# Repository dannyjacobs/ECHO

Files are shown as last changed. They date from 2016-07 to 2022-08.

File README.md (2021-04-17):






The External Calibrator for Hydrogen Arrays (ECHO) is a system for calibrating wide-field radio frequency arrays using a radio transmitter mounted on a drone.
Primarily targeting (but not exclusively limited to) arrays operating in the sub-GHz band targeting highly redshifted
21cm radiation from the early universe.

This repository contains software for planning missions and analyzing data. It also contains hardware designs for drones and mounts.

This is an open source project. Use and reuse is encouraged.  If you use this code or hardware designs please reference the github repo.
http://github.com/dannyjacobs/ECHO and cite [our 2017 paper](http://adsabs.harvard.edu/abs/2017PASP..129c5002J).  If you have improvements please fork and send a PR!

## Community
* We have an active "Slack Connect" channel, accessible to anyone with a Slack account.  To be invited, email [Danny Jacobs](dcjacob2@asu.edu)
* Project [Web page](http://danielcjacobs.com/ECHO)
* [Code Documentation](https://external-calibrator-for-hydrogen-arrays-echo.readthedocs.io)
* A [mailing list](https://groups.google.com/d/forum/astro_echo) exists

## Installation
Install prerequisites. We recommend the anaconda package manager
* healpy (note that as of Jan 2020 healpy is not available for Windows)
* matplotlib
* numpy
* scipy

Get this repo
`git clone https://github.com/dannyjacobs/ECHO.git`

Install using pip
```
cd ECHO
pip install .
```

## Organization
The code is organized into a few modules. The beam mapping pipeline steps are
1. Read and down-select drone telemetry
2. Read and down-select radio telescope data (varies per telescope, usually spectra vs time)
3. Match up drone positions and telescope measurements. (Sometimes referred to as zippering.)
4. Grid beam (including power map, sample counts and standard deviation)
5. Analyze results. Example analysis steps include:
  1. subtract transmitter model
  2. plot beam maps
  3. plot slices
  4. plot drone events and dynamics
  5. difference beams
### Modules

 #### `plot_utils.py`
 Functions for plotting, but also all functions relating to healpix gridding
 and manipulation including gridding.
  * `grid_to_healpix` :  grids aligned RF power vs XYZ position
 into a healpix map
  * `make_beam` :  downselects desired spectral channel, converts from latlon to XYZ and calls `grid_to_healpix`
  * `project_healpix` :  flattens from spherical healpix map to 2d gnomic projection
  * `rotate_hpm` :  rotates a healpix map about the polar axis. useful for plotting
  * Other functions, most of whom are deprecated.
 #### `read_utils.py`
 Functions for reading and writing drone and beam data. Drone log file formats
 are not well documented and change all the time.
  * `read_map` : replacement for healpy read function that respects nans
  * `write_map`: replacement for healpy write function that respect nans
  * `apm_version`: tries to determine the version of ardupilot that wrote a log file.
  * `read_apm_log_A_B_C` : reads an ardupilot log of version A_B_C
    * returns position_times, positions,
    * attitude_times, attitudes,
    * waypoint_times, waypoint_numbers
  * `read_echo_spectrum` : reads a spectrum data file output by the ECHO spectrum logger ca 2017 (signalhound + get_sh_spectra)
  * `read_orbcomm_spectrum` : reads a spectrum data file output by the Bradley orbcomm system (ca 2017)
  * `channel_select` : given a spectrum, list of frequencies, and desired frequency returns closest frequency and spectrum amplitude
  * `interp_rx`: interpolates received power onto the measured position time grid
  * `flag_angles` : flags outlier yaws input times,yaw_angles return matching flag array
  * `flag_waypoints` : flags a range of time around a list of waypoints
  * `apply_flagtimes` : Given a list of bad times, a buffer size and a time array, generate a flag table.
#### `position_utils.py`
 * `latlon2xy` : about what you think
 * `to_spherical` : xyz to spherical
#### `time_utils.py`
Most of these are of dubious necessity.
 * `unix_to_gps` : thin wrapper around astropy.Time
 * `gps_to_HMS` : convert GPS time to Hours Minutes Seconds, thin wrapper around
#### `server_utils.py`
Stuff developed to support real-time operations. This never worked very well with mavlink.
### Scripts
#### Jacobs 2017
Scripts used in the 2017 paper are all run in [one master shell script](https://github.com/dannyjacobs/ECHO_paper1/blob/master/scripts/make_plots.sh)
 * plot_yaw.py
 * plot_GB_pos_power_interp.py
 * ECHO_zipper.py
 * ECHO_mk_beam.py
 * plot_ECHO_GB_power_rms_counts.py
 * plot_ECHO_GB_maps.py
 * plot_GB_slices.py
 * ECHO_sub_tx_beam.py
 * plot_ECHO_GB_ratios.py
 * plot_GB_avg_slices.py
 * plot_MWAtile_slices.py
 * MWATilemodel2hpm.py
 * combine_MWAtile_maps.py

 #### Utility Scripts
  * valon_readwrite.py : program the valon transmitter
  * gen_spherical_flight_path.py : generate waypoints in a healpix pattern
  * CST_to_healpix.py : convert the beam file from CST Microwave studio to a healpix map. Note that this should eventually be replaced with [pyuvbeam](https://github.com/RadioAstronomySoftwareGroup/pyuvdata/blob/master/pyuvdata/uvbeam.py).

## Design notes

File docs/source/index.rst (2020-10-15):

.. ECHO documentation master file, created by
   sphinx-quickstart on Mon Jul 13 10:42:31 2020.
   You can adapt this file completely to your liking, but it should at least
   contain the root `toctree` directive.

Welcome to ECHO's documentation!
================================
ECHO is a drone-based system for calibrating wide-field radio arrays seeking to probe the Epoch of Reionization (EoR). The goal is to make accurate in-situ beam maps and incorporate this data into 21cm power spectrum analysis pipelines.
For more details you can read the first demonstration of ECHO paper by Jacobs et al. 2017 here_

This repository contains software used to generate flight plans, collect and reduce resulting data from a calibration run.

.. _here: https://ui.adsabs.harvard.edu/abs/2017PASP..129c5002J/abstract

Workflow
----------
Analysis of data from a calibration run involves three main steps:

* Reading in transmitter position data and receiver spectrum
* Interpolating receiver spectrum to drone flight times
* Gridding data onto a healpix map

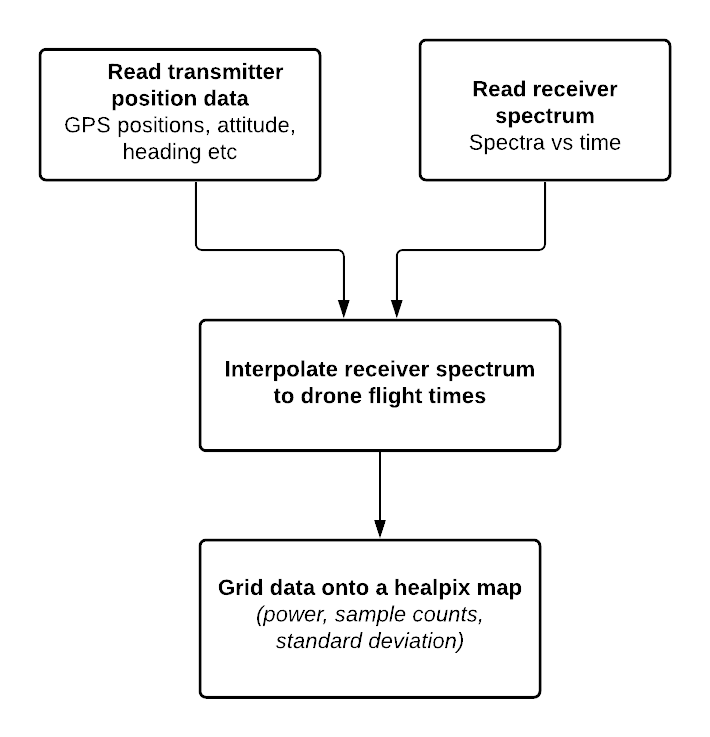
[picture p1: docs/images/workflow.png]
workflow


ECHO setup
------------

LWA-SV '19 setup

Flight Path
-----------------

ECHO follows a spherical shell flight pattern centered around the antenna under test as shown in the figure.

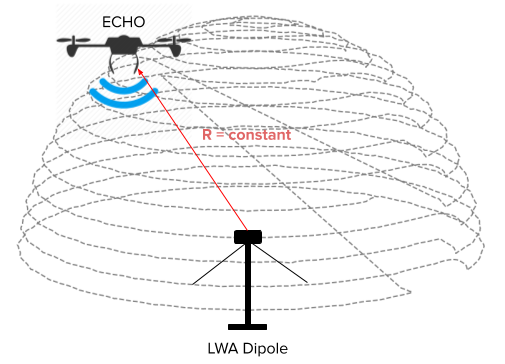
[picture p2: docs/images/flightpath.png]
flight path


.. toctree::
   :caption: Contents:

   Installation <installation>
   Tutorial <tutorial>
   API Reference <api>

Indices and tables
==================

* :ref:`genindex`
* :ref:`modindex`
* :ref:`search`

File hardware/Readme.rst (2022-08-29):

.. csv-table:: ECHO Version Summary
   :header: "Version", "Drone Make", "Drone Frame", "Drone Name", "Tx Mount", "Transmitter", "Antenna", "Flight Software"
   :widths: auto

   "1", "Mystery Inc.", "Octo", "Brain", " ", " ", "BicoLOG 5070", " "
   "2", "Flamewheel", "Quad", "Crater", " ", " ", "BicoLOG 5070", " "
   "3", "3D-Robotics", "X8", Pancake, " ", " ", BicoLOG 5070", " "
   "4", "3D-Robotics", "X8", Waffle, "`Sliding_Mount <https://github.com/dannyjacobs/ECHO/tree/master/hardware/STLs/04_Sliding_Mount>`_", "Blackbox", BicoLOG 5070", " "
   "5", "3D-Robotics", "X8", Killer, "`X8_Mount_v1 <https://github.com/dannyjacobs/ECHO/tree/master/hardware/STLs/05_X8_Mount_v1>`_", "Blackbox", BicoLOG 5070", " "
   "6", "Steadidrone Vader", "X8", "Vader", "`Vader_Mount <https://github.com/dannyjacobs/ECHO/tree/master/hardware/STLs/06_Vader_Mount>`_", "Blackbox", "BicoLOG 5070", "PX4"
   "7", "Yuneec", "Octo H520", "Yuneec", "`Yuneec_Mount <https://github.com/dannyjacobs/ECHO/tree/master/hardware/STLs/07_Yuneec_Mount>`_", "Valon 5009", "BicoLOG 5070", "Yuneec"
   "8", "3D-Robotics", "X8", "Killer", "`X8_Mount_v2 <https://github.com/dannyjacobs/ECHO/tree/master/hardware/STLs/08_X8_Mount_v2>`_", "Valon 5009", "BicoLOG 5070", "PX4"
   "9", "in house `bom <https://github.com/dannyjacobs/ECHO/blob/master/hardware/Chiropter%20BoM%20-%20Revised%20Build%20Sheet.pdf>`_, `build log <https://github.com/dannyjacobs/ECHO/blob/master/hardware/Chiropter%20Build%20Log.pdf>`_","Hex F550", "Chiropter", "`Chiropter Mount v1 (for Valon) <https://github.com/dannyjacobs/ECHO/tree/master/hardware/STLs/09_Chiropter_Mount_v1>`_, `Mount V2 for TituTx etc  <https://github.com/dannyjacobs/ECHO/tree/master/hardware/STLs/10_Chiropter_Mount_v2>`_","Valon 5009","BicoLOG 5070","PX4"

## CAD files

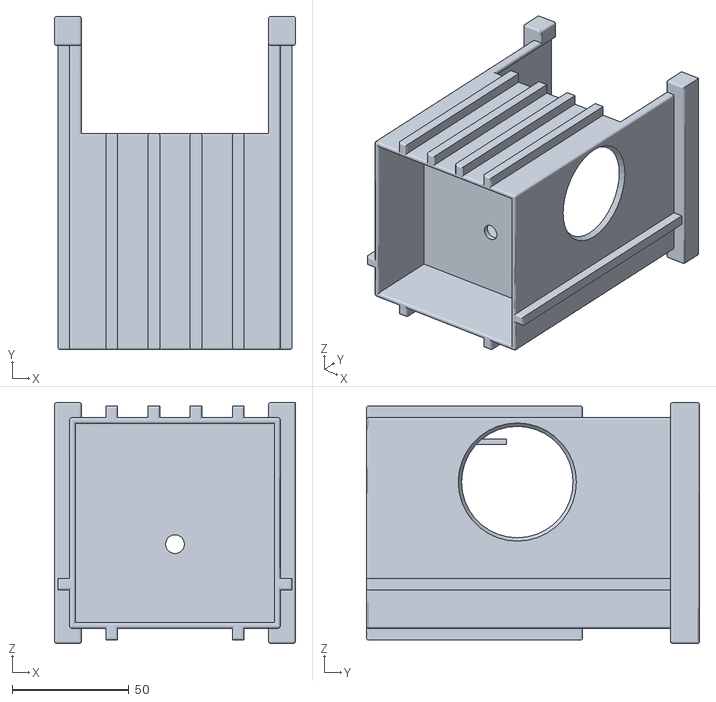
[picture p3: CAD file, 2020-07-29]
hardware/STLs/04_Sliding_Mount/Sliding_Mount_Bottom.STL
103.0 x 142.5 x 103.0

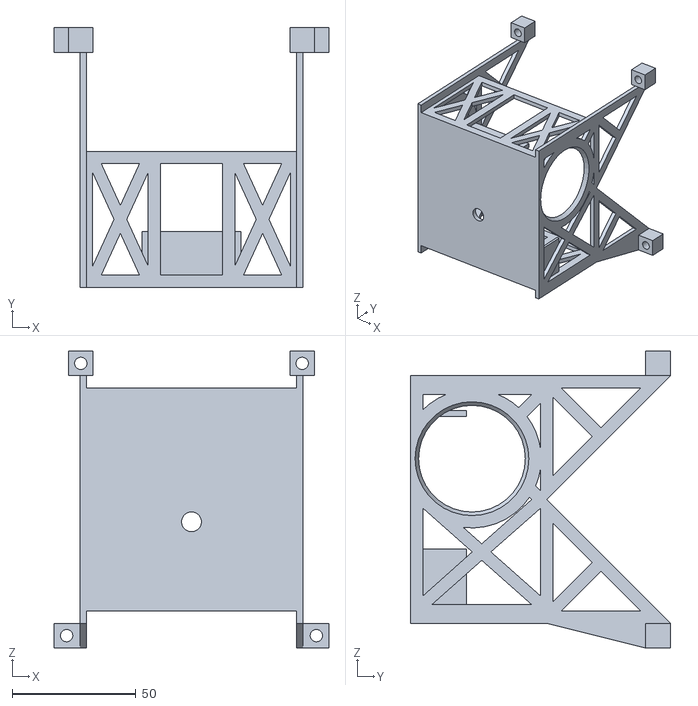
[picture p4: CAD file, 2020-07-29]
hardware/STLs/05_X8_Mount_v1/X8_Mount_v1.STL
111.0 x 105.0 x 120.1

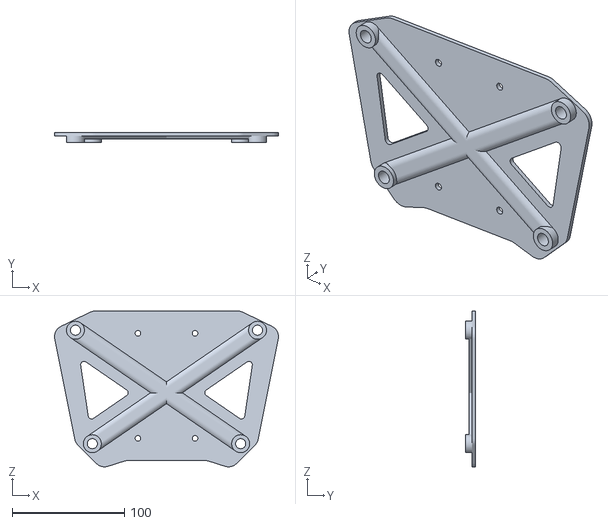
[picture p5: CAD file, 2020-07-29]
hardware/STLs/06_Vader_Mount/Vader_Adapter_Plate.STL
199.3 x 9.00 x 138.6

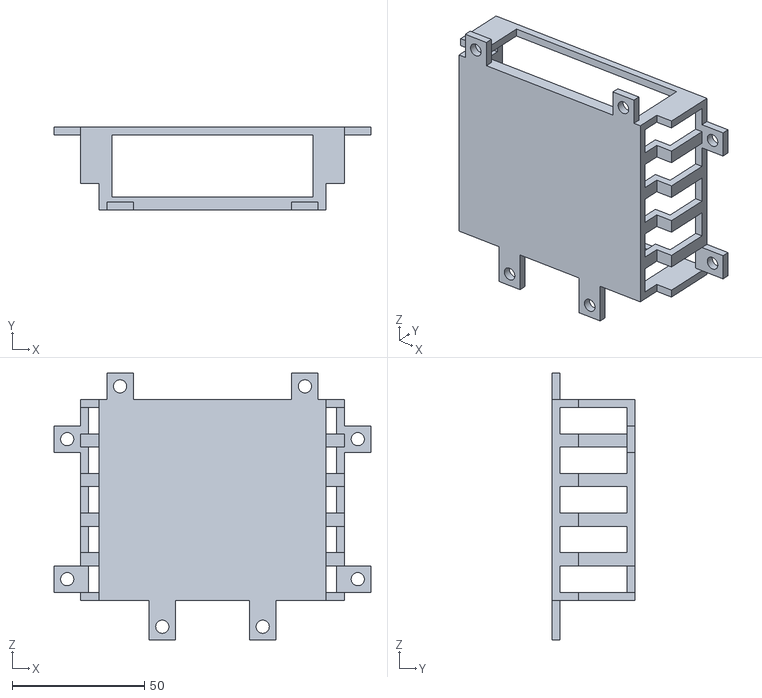
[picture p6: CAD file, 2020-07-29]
hardware/STLs/07_Yuneec_Mount/Yuneec_Valon_Mount.STL
120.0 x 31.5 x 101.0

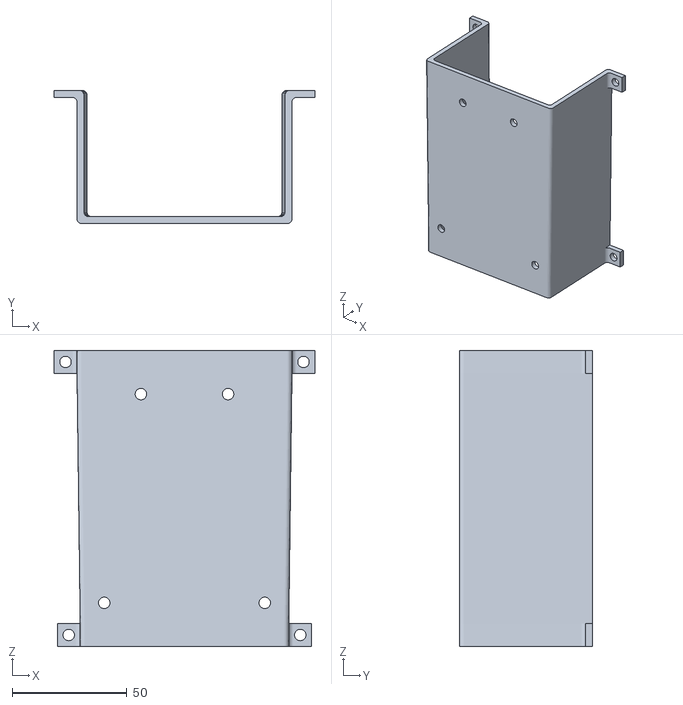
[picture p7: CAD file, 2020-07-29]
hardware/STLs/08_X8_Mount_v2/X8_Adapter_Plate.STL
113.8 x 58.0 x 129.1

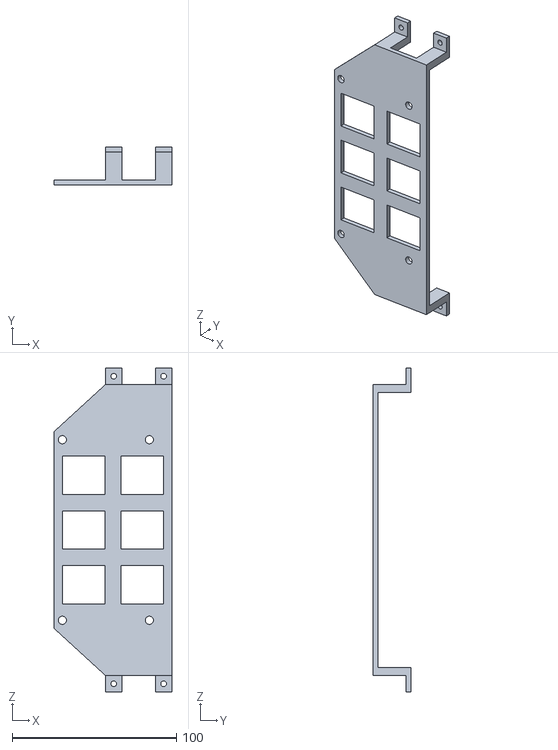
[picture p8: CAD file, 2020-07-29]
hardware/STLs/09_Chiropter_Mount_v1/Chiropter_Adapter_Plate_v1.STL
71.7 x 23.0 x 197.4

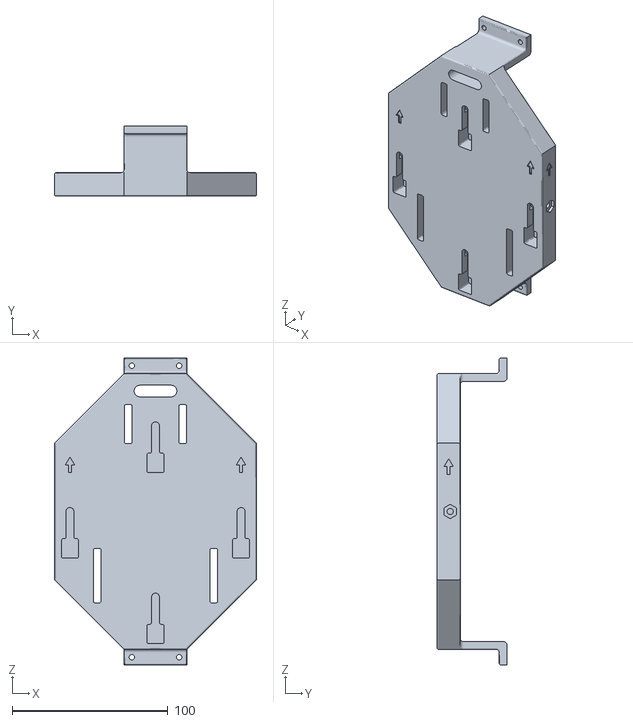
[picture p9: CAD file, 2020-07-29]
hardware/STLs/10_Chiropter_Mount_v2/Chiropter_Adapter_Plate_v2.2.STL
130.0 x 45.0 x 197.4

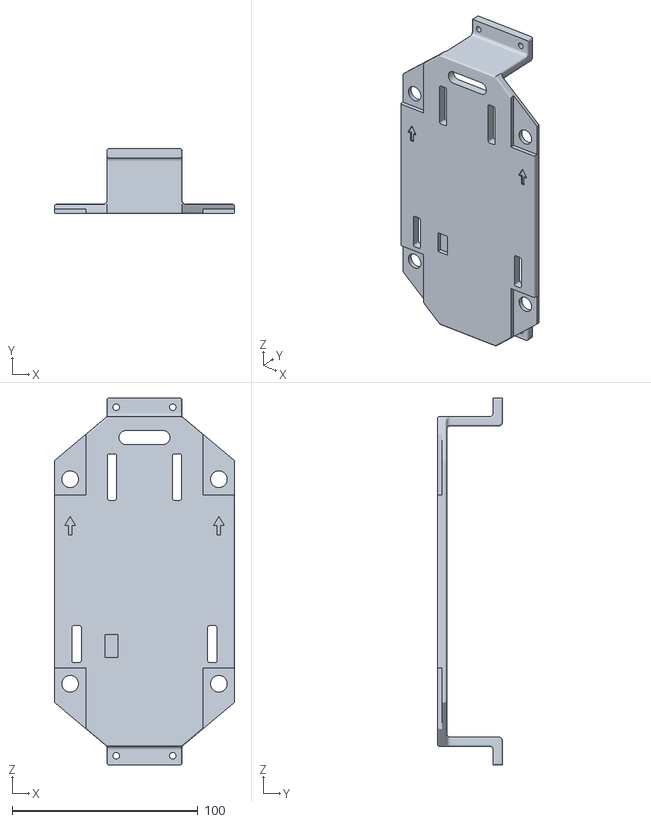
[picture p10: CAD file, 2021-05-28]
hardware/STLs/11_Modular_Chiropter_Mount/Chiropter_Adapter_Plate_v5.STL
97.0 x 35.0 x 197.4

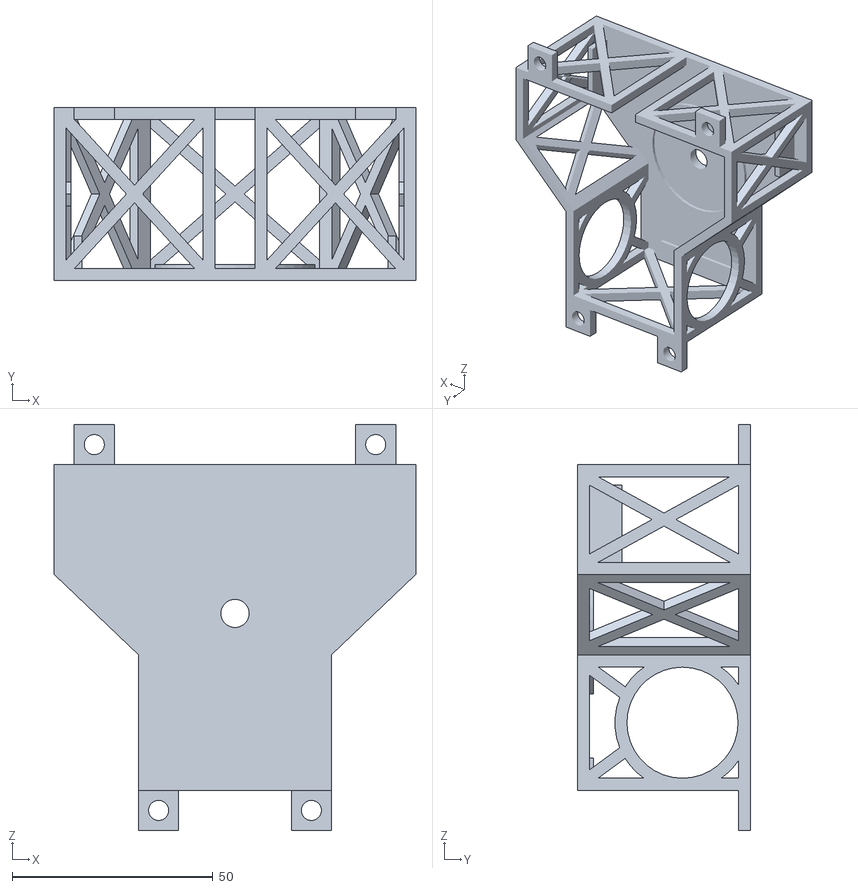
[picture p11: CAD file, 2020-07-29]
hardware/STLs/Generic_BicoLOG_Mount.STL
90.0 x 43.0 x 101.0

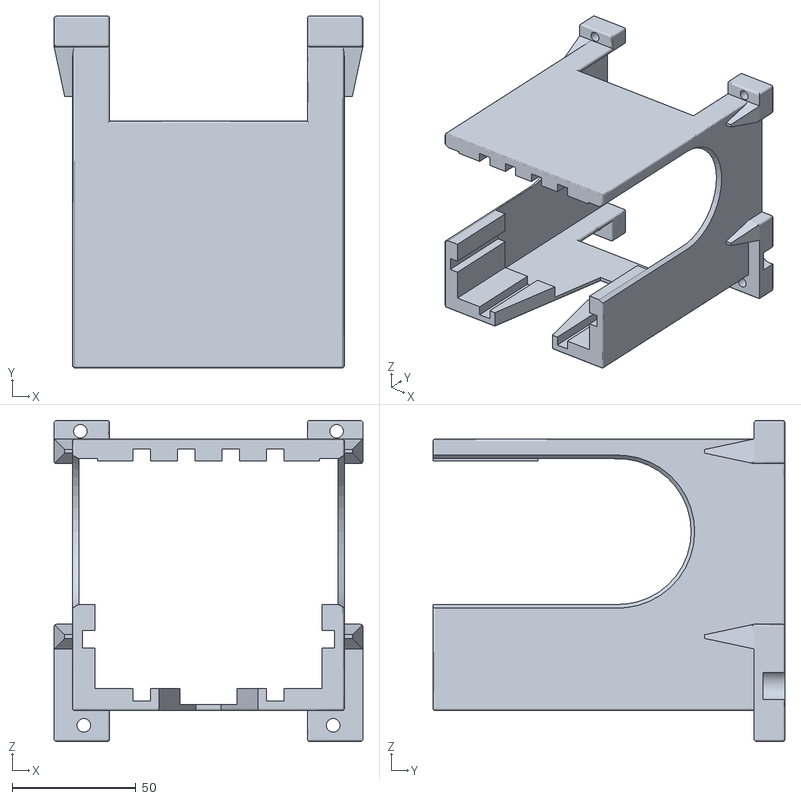
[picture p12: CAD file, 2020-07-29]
hardware/STLs/04_Sliding_Mount/Sliding_Mount_Top.STL
125.0 x 142.5 x 130.0

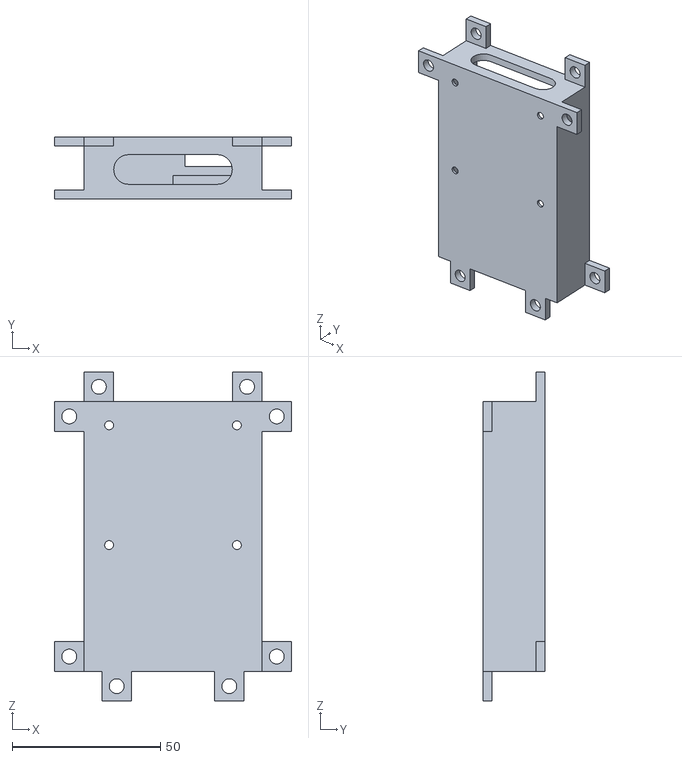
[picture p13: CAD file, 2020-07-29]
hardware/STLs/06_Vader_Mount/Vader_Valon_Mount.STL
80.0 x 21.0 x 111.0

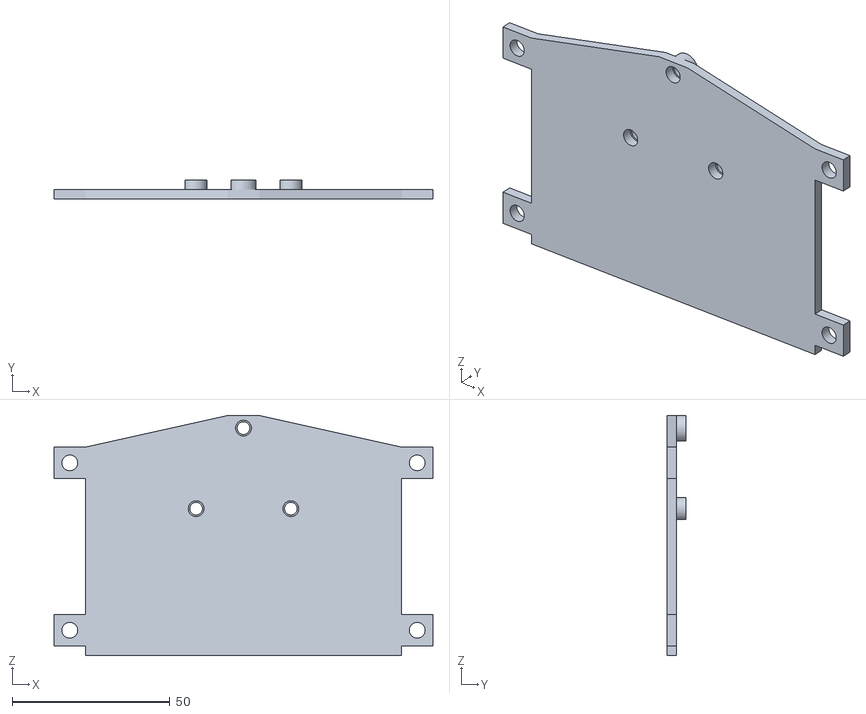
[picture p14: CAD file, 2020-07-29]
hardware/STLs/07_Yuneec_Mount/Yuneec_Adapter_Plate.STL
120.0 x 6.00 x 76.0

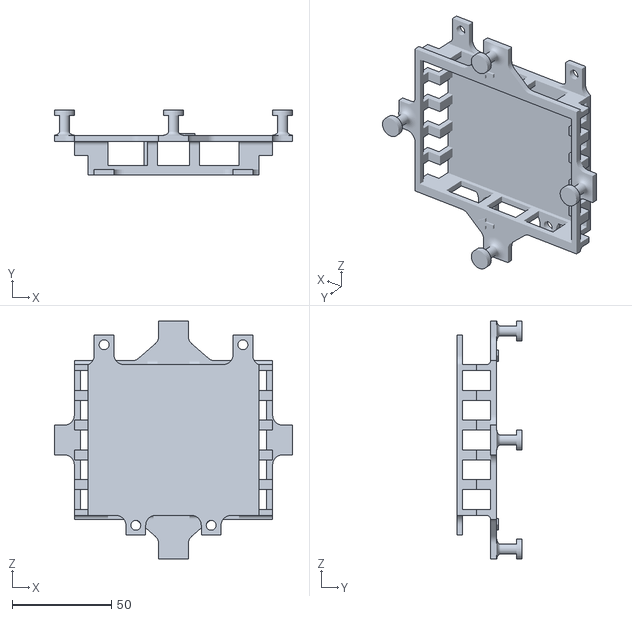
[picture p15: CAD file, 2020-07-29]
hardware/STLs/10_Chiropter_Mount_v2/Valon_Mount_v2.2.STL
120.0 x 33.0 x 120.0

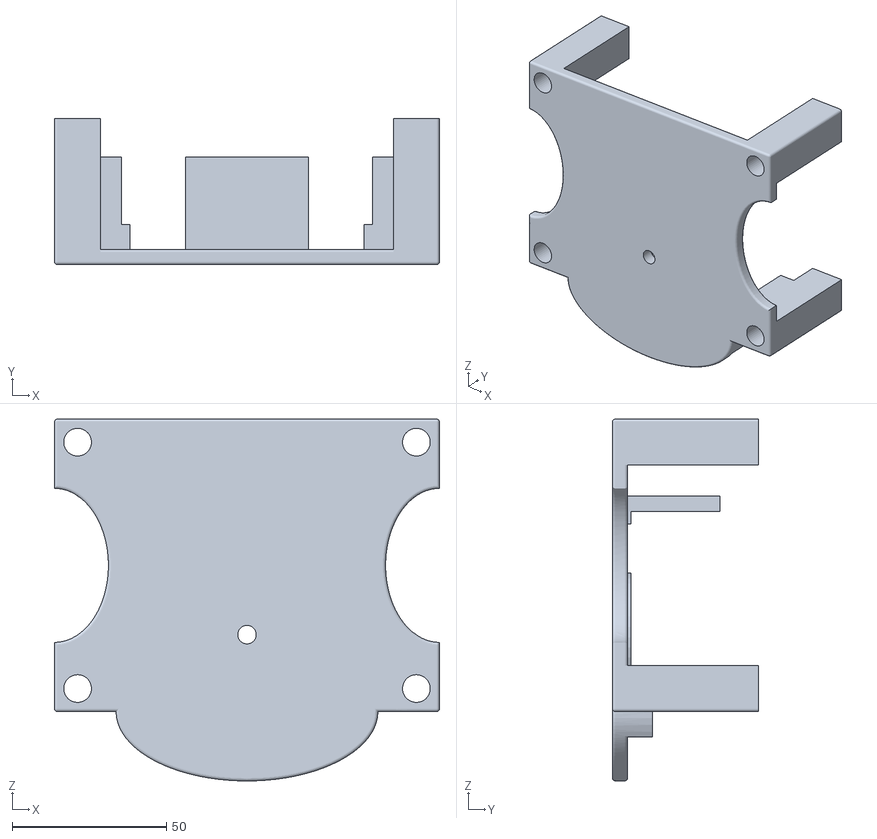
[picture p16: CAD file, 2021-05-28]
hardware/STLs/11_Modular_Chiropter_Mount/BicoLOG_Module_v5.STL
125.0 x 47.5 x 117.5

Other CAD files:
hardware/STLs/09_Chiropter_Mount_v1/Chiropter_Valon_Mount_v1.STL
hardware/STLs/06_Vader_Mount/Vader_Anker_Mount.STL
hardware/STLs/11_Modular_Chiropter_Mount/Payload_Module_v5.STL

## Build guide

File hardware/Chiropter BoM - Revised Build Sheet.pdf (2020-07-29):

Component | Quantity | Price/Unit | Weight/Unit (g) | Link | Notes
Tarot 690S Frame | 1 | $123.40 | 600 | https://www.banggood.com/Tarot-FY690S-Full-6-Axis-Folding-Rack-Carbon-Fiber-Frame-TL68C01-p-86635.html?akmClientCountry=America&cur_warehouse=CN F550 was too small. Weight estimated.
DJI E800 Propulsion System (6) | 1 | $479.00 | 1008 | https://www.amazon.com/E800-Motor-props-Accessories-Updater/dp/B00V32GF2Q Unavailable from DJI. 2100g/rotor thrust.
Pixhawk 2.1 | 1 | $247.99 | 39 | https://www.getfpv.com/pixhawk-2-1-standard-set.html?utm_source=google&utm_medium=cpc&adpos=1o1&scid=scplp8181&sc_intid=8181&gclid=CjwKCAjw0N3nBRBvEiwAHMwvNrSo92YSUxTHLvcFoZUWNv6_KPdrRPRKvx6o2IDv4lYmDTGwdjcMaxoC8REQAvD_BwE Weight taken from JD's 2018 CPS drone BoMs.
Here+ RTK GPS Set | 1 | $600.00 | 131 | https://www.spektreworks.com/products/here-plus-gps-kit Weight taken from JD's 2018 CPS drone BoMs.
Frsky X8R Receiver | 1 | $33.99 | 17 | https://www.getfpv.com/frsky-x8r-16ch-receiver-sbus-smart-port-amplified-pcb-antenna.html?gclid=Cj0KCQjwrdjnBRDXARIsAEcE5YlvUxqDHbKJj86G3-96jxNP-Mor0R8OZrp-bm6nJF_LLq9iIiKAnmEaAr22EALw_wcB
Readymade X8R Cable | 1 | $19.99 | 3 | http://www.craftandtheoryllc.com/store/ct-telemetry-cable-for-frsky-radios/
Holybro 915MHz Radio (2pack) | 1 | $39.00 | 20 | https://www.getfpv.com/holybro-100mw-transceiver-telemetry-radio-set-v3-915mhz.html?utm_source=google&utm_medium=cpc&adpos=1o1&scid=scplp8989&sc_intid=8989&gclid=Cj0KCQjwrdjnBRDXARIsAEcE5YkdN6Xqia0bzJkTYvNfe-hgE1NqSV8UITNlHUZsgZ2QVQkgOVTSTlsaAu4aEALw_wcB Weight estimated. 2 included in pack.
6S 16000mAh Battery | 1 | $325.79 | 1932 | https://www.genstattu.com/tattu-16000mah-15c-6s1p-lipo-battery-pack-with-ec5-plug.html Considering 16/22Ah and 4S/6S. 6S 22Ah had best ecalc performance.
Mauch 4-14s Battery Kit | 1 | $89.90 | 110 | http://www.craftandtheoryllc.com/store/mauch-4-14s-premium-line-single-battery-kit-voltage-current-sensor-regulated-power-supply/#configuration
GPS Mount | 1 | $8.45 | 10 | https://www.ebay.com/p/GPS-Antenna-Mount-Folding-Bracket-Anodized-Aluminum-Carbon-for-APM-Pixhawk/17015554216?iid=253451907935 Weight estimated.
Total Price | Total Weight
$1,967.51 | 3870
Total Thrust | Thrust/Weight
9600 | 2.480620155

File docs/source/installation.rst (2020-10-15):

.. ECHO documentation master file, created by
   sphinx-quickstart on Mon Jul 13 10:42:31 2020.
   You can adapt this file completely to your liking, but it should at least
   contain the root `toctree` directive.

.. highlight:: python

Installation
================================

To install ECHO, clone the repository ::

    git clone https:github.com/dannyjacobs/ECHO

Naviagte to the to the ECHO folder ::

    cd ECHO
    pip install .

Dependencies
--------------

we recommend the anaconda package manager.

- healpy (note that as of Jan 2020, healpy is not available for Windows)
- numpy
- scipy
- astropy
- matplotlib

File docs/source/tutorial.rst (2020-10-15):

.. ECHO documentation master file, created by
   sphinx-quickstart on Mon Jul 13 10:42:31 2020.
   You can adapt this file completely to your liking, but it should at least
   contain the root `toctree` directive.

.. highlight:: python

Tutorial
================================
Analysis of data from a calibration run involves three main steps:

* Reading in transmitter position data and receiver spectrum
* Interpolating receiver spectrum to drone flight times
* Gridding data onto a healpix map

A mapping run is split into smaller chunks of flight aka 'sorties' owing to the battery life of the drone. Each of these sorties is associated with a transmitter position file and a receiver spectrum.

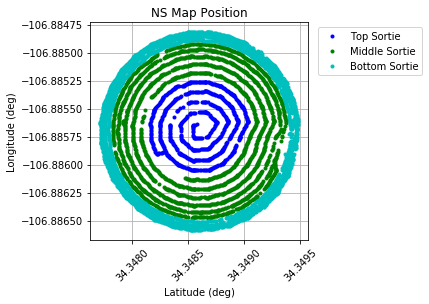
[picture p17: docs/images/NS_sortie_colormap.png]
flight path


    2D plot of a hemispherical flight pattern.

Reading in transmitter position data
---------------------------------------
Transmitter position is derived from drone logs. These logs come in two data formats: tlog and ulog format.

* Tlogs are telemetry logs recorded by the ground station when the drone is powered on and connected.
* Ulogs are position logs saved on the drone's SD card.

Two functions read_tlog_txt_ and read_ulog_ are available on ECHO.readutils to extract transmitter position data from these log files.

.. _read_tlog_txt: api.html#ECHO.read_utils.read_tlog_txt
.. _read_ulog: api.html#ECHO.read_utils.read_ulog

Reading in receiver spectrum
------------------------------
Data formats of receiver spectrum files  may vary with the telescope but usually, it is a hdf5 file containing spectra vs time.

Receiver spectrum files can be read-in using read_h5_ function from ECHO.readutils.

.. _read_h5: api.html#ECHO.read_utils.read_h5

Matching up receiver spectrum with drone flight times
-------------------------------------------------------

We begin with instantiating an Observation Object and pass in coordinates of antenna under test (AUT), programmed frequency of transmitter in MHz and a short description of AUT ::

    import ECHO

    NS_Obs = ECHO.Observation(lat=34.3486, lon=-106.8857, frequency=70, description='LWA Antenna 137')

We define paths to the files associated with each sortie :

::

    datadir = '/LWA_October_2019/data/'

    NS_Obs.addSortie(
        tlog=datadir+"tlog_data/NSMap_MiddleSortie.txt",
        ulog=datadir+"ulog_data/NSMap_MiddleSortie.ulg",
        data=datadir+"LWA_spectra/NS_Sorties/01_NSmap_MidSortie_waterfall.hdf5",
        sortie_title="NS Mid"
        )

To read these files, we call the read_sorties() function ::

    NS_Obs.read_sorties()

The data is stored in dictionaries and can be accessed as : ::

    print(NS_Obs.sortie_list[0].t_dict.keys())
    print(NS_Obs.sortie_list[0].u_dict.keys())

Additional sorties can be added to a single observation using the addSortie() function ::

    #add two additional sorties
    NS_Obs.addSortie(
        tlog=datadir+"tlog_data/NSMap_TopSortie_Repeat.txt",
        ulog=datadir+"ulog_data/NSMap_TopSortie_Repeat.ulg",
        data=datadir+"LWA_spectra/NS_Sorties/03_NSmap_TopSortie_waterfall.hdf5"
        )

    NS_Obs.addSortie(
        tlog=datadir+"tlog_data/NSMap_BottomSortie.txt",
        ulog=datadir+"ulog_data/NSMap_BottomSortie.ulg",
        data=datadir+"LWA_spectra/NS_Sorties/02_NSmap_BotSortie_waterfall.hdf5"
        )

    #read in all of the current sorties, apply bootstart correction, and flag the start/endpoints
    for sortie in NS_Obs.sortie_list:
        sortie.read() #Note that this replaces all previous reads
        sortie.apply_bootstart()
        sortie.flag_endpoints()

    #takes the data from all sorties, sorts them by time, and combines them into a single array
    NS_Obs.combine_sorties()

Matching up telescope data to drone positions
-------------------------------------------------

Telescopes record data at a higher rate than a gps module on the drone. To match up the telescope data to the drone positions, we downselect and interpolate telescope data.
::

    #combine the drone position data with the intrument response
    NS_Obs.interpolate_rx(1,1,'XX')

Gridding data
-------------------------------

A common way to store beam models in 21cm pipelines is to use the HEALPix pixelization scheme. Hence, we'll be gridding our data onto a healpix map.

To do so, we create a Beam object ::

    NS_Obs.make_beam()

Once the beam object is created, the healpix map can be visualised by executing ::

    NS_Obs.plot_beam()

Analysis
-----------

* E and H planes of the beammap can be plotted by executing ::

    NS_Obs.plot_slices(figsize=(10,10))

* ECHO uses pyuvbeam to read-in CST export files of the transmitter beam.

To do so instantiate a Beam object with beam_type = 'efield' or 'power' and call the read_cst_beam()::

    tx_beam = ECHO.Beam(beam_type= 'efield')
    CST_file = '../Chiropter_NS_PECBico_ff70_ZupYnull.txt'
    tx_beam.read_cst_beam(CST_file, beam_type='efield', frequency=[70e6],
                   telescope_name='Chiropter', feed_name='BicoLOG', feed_version='1.0',
                   model_name = 'Chiropter_NS_2019', model_version='1.0', feed_pol='y')

To plot the cst beam: ::

    tx_beam.plot_efield()

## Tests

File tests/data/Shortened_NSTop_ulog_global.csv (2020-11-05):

timestamp | lat | lon | alt | alt_ellipsoid | delta_alt | vel_n | vel_e | vel_d | yaw | eph | epv | terrain_alt | lat_lon_reset_counter | alt_reset_counter | terrain_alt_valid | dead_reckoning
143941884 | 34.3492408931479 | -106.88581799167837 | 1477.1158 | 1450.921 | -0.0 | -0.026761366 | -0.0017877584 | -0.013919022 | -0.09170324 | 0.9186021 | 1.3707787 | 0.0 | 2 | 0 | 0 | 0
144141877 | 34.349240847100674 | -106.88581800723917 | 1477.1202 | 1450.9218 | -0.0 | -0.026344912 | -0.0035520296 | -0.014359278 | -0.09156849 | 0.9185409 | 1.3708763 | 0.0 | 2 | 0 | 0 | 0
144350678 | 34.34924079073418 | -106.8858180210184 | 1477.1185 | 1450.9169 | -0.0 | -0.027068885 | -0.004169931 | -0.013727835 | -0.09147434 | 0.91878563 | 1.3707806 | 0.0 | 2 | 0 | 0 | 0
144549077 | 34.34924072993843 | -106.88581802995677 | 1477.1216 | 1450.917 | -0.0 | -0.027806597 | -0.0051411623 | -0.01442604 | -0.09121436 | 0.91874826 | 1.3708674 | 0.0 | 2 | 0 | 0 | 0
144757077 | 34.349240661439815 | -106.88581803947686 | 1477.1312 | 1450.9233 | -0.0 | -0.028565595 | -0.0054902914 | -0.016312702 | -0.09082295 | 0.9189275 | 1.3707577 | 0.0 | 2 | 0 | 0 | 0
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

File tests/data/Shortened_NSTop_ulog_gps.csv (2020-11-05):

timestamp | time_utc_usec | lat | lon | alt | alt_ellipsoid | s_variance_m_s | c_variance_rad | eph | epv | hdop | vdop | noise_per_ms | jamming_indicator | vel_m_s | vel_n_m_s | vel_e_m_s | vel_d_m_s | cog_rad | timestamp_time_relative | heading | heading_offset | fix_type | vel_ned_valid | satellites_used
143816108 | 1572029841799795 | 343492408 | -1068858180 | 1475235 | 1450738 | 0.17500001 | 0.7112686 | 0.528 | 0.814 | 0.78 | 1.2099999 | 107 | 12 | 0.025 | 0.015000001 | -0.020000001 | -0.030000001 | 3.3064876 | 0 | nan | 0.0 | 3 | 1 | 14
144016362 | 1572029841999796 | 343492408 | -1068858180 | 1475240 | 1450743 | 0.14600001 | 0.7112743 | 0.528 | 0.813 | 0.78 | 1.2099999 | 107 | 12 | 0.027 | -0.025 | -0.009000001 | -0.015000001 | 3.3064876 | 0 | nan | 0.0 | 3 | 1 | 14
144212154 | 1572029842199795 | 343492407 | -1068858180 | 1475257 | 1450760 | 0.19000001 | 0.71128166 | 0.528 | 0.813 | 0.78 | 1.2099999 | 107 | 12 | 0.010000001 | -0.009000001 | 0.004 | -0.017 | 3.3064876 | 0 | nan | 0.0 | 3 | 1 | 14
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

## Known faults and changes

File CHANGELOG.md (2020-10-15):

# Changelog

All notable changes to this project will be documented in this file.

The format is based on [Keep a Changelog](https://keepachangelog.com/en/1.0.0/),
and this project adheres to [Semantic Versioning](https://semver.org/spec/v2.0.0.html).

## [Unreleased]
### Added
- ReadTheDocs support, can now be read at: https://external-calibrator-for-hydrogen-arrays-echo.readthedocs.io
- Initial RtD tutorial added
- Added list of drone iterations with build logs and solid model files. Table in hardware/echo_hardware_summary.rst
- Class created for Beams, allows reading and writing of both drone and instrument beams
- Requirements.txt created, all modules now referenced there during setup
- Additional plotting functions for beams: orthview, E and H slices, polar plots, mollview
- Preliminary files for CircleCI

### Changed
- Observations and Beam functions split into separate files (observations.py, beams.py)
- Beam functions now check for appropriate beam types
- Bugfixes for beam functions
- Editing to docstrings, placed in Google format (https://google.github.io/styleguide/pyguide.html#38-comments-and-docstrings)

### Removed
- Python 2.7 support and testing (not compatible with astropy)

## [0.0.1] - 2020-02-03
### Added
- Changelog
- Test subfolders and empty test files
- keep/ directory for scripts, will move when finalized
- basic test CI infrastructure and GitHub action

### Changed
- testing/ directory renamed to tests/
- edited setup.py to include dependencies and tests

### Removed
- Drone RFI report
- ECHO Reduction

## [0.0.1] - 2020-10-08
### Added
- Documentation and Tutorial for usage

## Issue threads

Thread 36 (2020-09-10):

### ISSUE TITLE
plot_polar() function in observations.py 

### ISSUE THREAD

**Issue by mrudula-gopalkrishna** [dannyjacobs/ECHO#36]
plot_polar() currently seems to only works for altitude= 0.

Also not sure what this piece of code intended to do:  
`alt[:]=altitude*np.pi/2 `

**Comment by dmlewis9** [comment]
Hmmm, it seems to only work with certain altitudes. I'm working on figuring out a fix.

Also that line simply converts the decimal altitude into radians.

**Comment by dmlewis9** [comment]
Fixed in https://github.com/dannyjacobs/ECHO/commit/02512b286ee71829c630926877a34902e9d8b5e1, function should work properly now.

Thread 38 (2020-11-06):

### ISSUE TITLE
We need good test data for unit testing

### ISSUE THREAD

**Issue by dmlewis9** [dannyjacobs/ECHO#38]
I'll start by doing a few manual tests using the current datafiles, but we need to make a couple of small files to better allow comprehensive unit testing.

[ ] tlog
[ ] ulog
[ ] rx data
[ ] cst

**Comment by mickeyhorn** [comment]
The zip below contains tlog and ulog data trimmed down to the first few seconds to be below 50kB. They cover approximately the same amount of time, but at different step sizes, hence the difference in file size. It also contains an appropriate CST export model for the Chiropter at 70MHz.

I slacked David the rx data separately because it is in .hdf5 format, which is both too large for github and untrimmable (to my knowledge).
[Small_Test_Logs.zip](https://github.com/dannyjacobs/ECHO/files/5228264/Small_Test_Logs.zip)

**Comment by dmlewis9** [comment]
Appropriate data files added for testing. HDF5 data trimmed down to a manageable size.

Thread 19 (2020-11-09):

### ISSUE TITLE
Need suite of tools to analyze beams from CST

### ISSUE THREAD

**Issue by mickeyhorn** [dannyjacobs/ECHO#19]
**Currently Have/Using:**
_CST_to_healpix.py_ script in this repo :: converts CST export file to healpix fits files
_Drone_CSTBeam_HealpixPlots_ jupyter notebook in Mickey's Dropbox workspace :: converts CST export file to mollviews, gridded views, and slices
_vivaldi_beam_compare_ jupyter notebook sent by Honggeun :: plots mollviews and does differencing between beams
_plot_slices.py_ script in this repo (old) :: makes slices from healpix fits files

**We Want:**
Mollviews
Gridded Views (maybe from top and bottom?)
Polar Cuts (with ability to tweak theta and phi viewing angles)
1D Slices (e-plane and h-plane)
Ability to difference beams and view all above plots
Plot both directivity and gain (ieee)

**Comment by dmlewis9** [comment]
all implemented except for beam differencing and directivity/gain plots

**Comment by dmlewis9** [comment]
Make a ReadTheDocs tutorial to explain beam manipulation and create plots.

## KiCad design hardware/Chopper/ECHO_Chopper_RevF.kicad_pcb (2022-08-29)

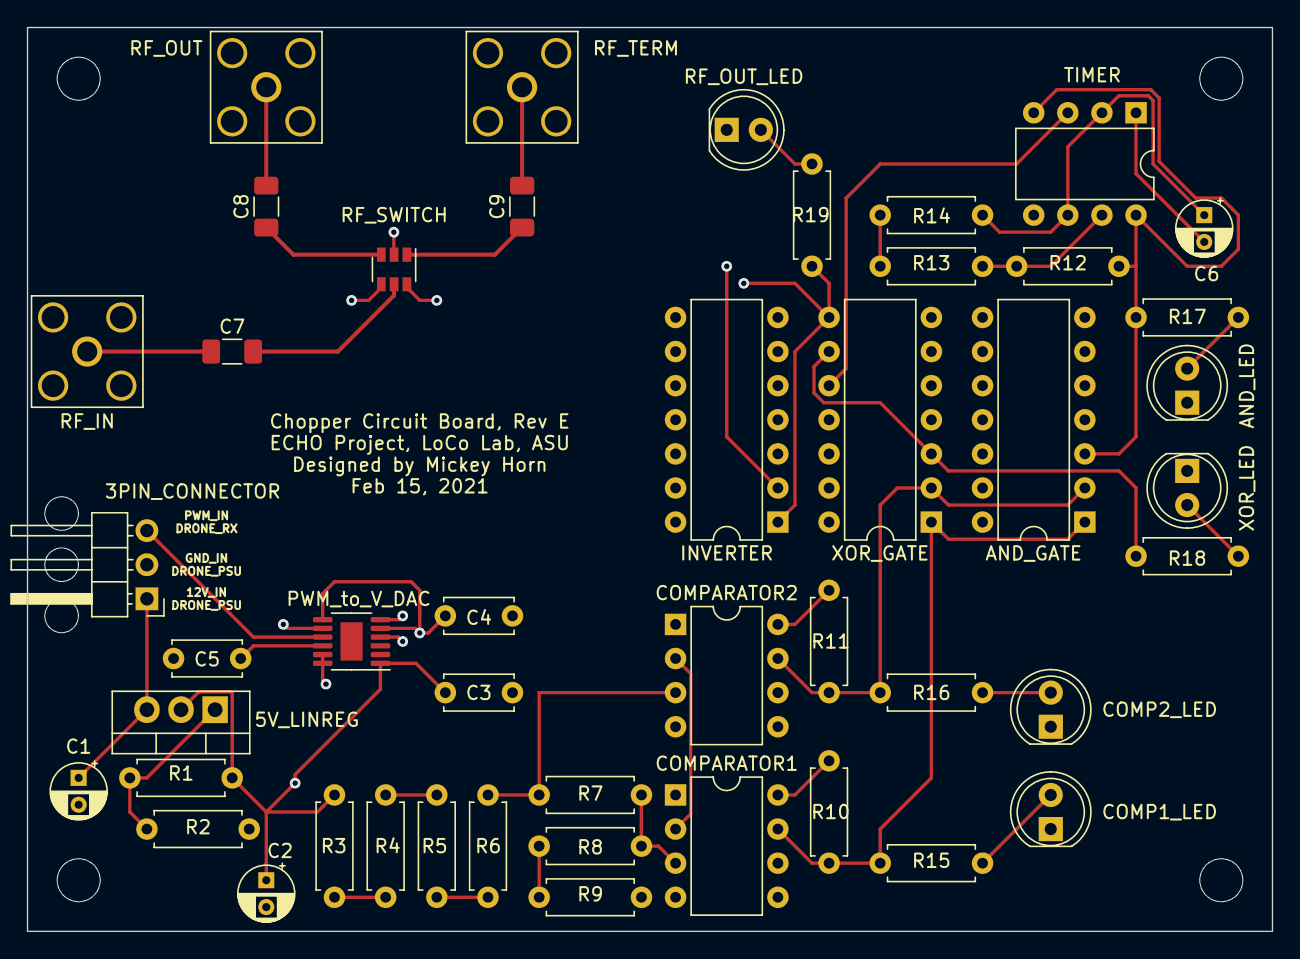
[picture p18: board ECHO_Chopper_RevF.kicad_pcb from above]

Board: 4 copper layers, 92.7 x 67.3 mm, 46 parts (0 on the bottom side), 34 nets.

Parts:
3PIN_CONNECTOR: Conn_01x03_Male; PinHeader_1x03_P2.54mm_Horizontal
5V_LINREG: LM317_3PinPackage; TO-220-3_Vertical
AND_GATE: SN74LS08N; DIP-14_W7.62mm
AND_LED: LED; LED_D5.0mm
C1: 0.1uF; CP_Radial_D4.0mm_P2.00mm
C2, C6: 1uF; CP_Radial_D4.0mm_P2.00mm
C3, C4, C5: 0.15uF; C_Disc_D5.0mm_W2.5mm_P5.00mm
C7, C8, C9: 390pF; C_1206_3216Metric_Pad1.33x1.80mm_HandSolder
COMP1_LED, COMP2_LED: LED; LED_D5.0mm
COMPARATOR1, COMPARATOR2: LM311; DIP-8_W7.62mm
INVERTER: SN74LS04N; DIP-14_W7.62mm
PWM_to_V_DAC: LTC2644CMS-L12#PBF; MSOP-12-1EP_3x4mm_P0.65mm_EP1.65x2.85mm
R1, R15, R16, R17, R18, R19: 100; R_Axial_DIN0207_L6.3mm_D2.5mm_P7.62mm_Horizontal
R2: 300; R_Axial_DIN0207_L6.3mm_D2.5mm_P7.62mm_Horizontal
R3, R14: 100k; R_Axial_DIN0207_L6.3mm_D2.5mm_P7.62mm_Horizontal
R4: 47k; R_Axial_DIN0207_L6.3mm_D2.5mm_P7.62mm_Horizontal
R5: 22k; R_Axial_DIN0207_L6.3mm_D2.5mm_P7.62mm_Horizontal
R6: 5.6k; R_Axial_DIN0207_L6.3mm_D2.5mm_P7.62mm_Horizontal
R7: 2.2k; R_Axial_DIN0207_L6.3mm_D2.5mm_P7.62mm_Horizontal
R8, R9: 3.3k; R_Axial_DIN0207_L6.3mm_D2.5mm_P7.62mm_Horizontal
R10, R11: 20k; R_Axial_DIN0207_L6.3mm_D2.5mm_P7.62mm_Horizontal
R12: 15k; R_Axial_DIN0207_L6.3mm_D2.5mm_P7.62mm_Horizontal
R13: 200k; R_Axial_DIN0207_L6.3mm_D2.5mm_P7.62mm_Horizontal
RF_IN: Valon Input; SMA_Amphenol_132203-12_Horizontal
RF_OUT: BicoLOG Output; SMA_Amphenol_132203-12_Horizontal
RF_OUT_LED: LED; LED_D5.0mm
RF_SWITCH: HMC545AE; SOT-23-6
RF_TERM: Terminated Output; SMA_Amphenol_132203-12_Horizontal
TIMER: TLC555xP; DIP-8_W7.62mm
XOR_GATE: SN74LS86AN; DIP-14_W7.62mm
XOR_LED: LED; LED_D5.0mm

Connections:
/0.18V: COMPARATOR1.3, R7.2, R8.1
/0.24V: COMPARATOR2.3, R6.2, R7.1
/5V: 5V_LINREG.2, AND_GATE.14, C2.1, C3.1, C4.1, COMPARATOR1.8, COMPARATOR2.8, INVERTER.14, PWM_to_V_DAC.1, PWM_to_V_DAC.5, PWM_to_V_DAC.7, R1.1, R3.1, R10.2, R11.2, XOR_GATE.14
/12V: 3PIN_CONNECTOR.1, 5V_LINREG.3, C1.1
/PWM: 3PIN_CONNECTOR.3, PWM_to_V_DAC.9
GND: 3PIN_CONNECTOR.2, AND_GATE.7, AND_LED.1, C1.2, C2.2, C3.2, C4.2, C5.2, C6.2, COMP1_LED.1, COMP2_LED.1, COMPARATOR1.1, COMPARATOR1.4, COMPARATOR2.1, COMPARATOR2.4, INVERTER.7, PWM_to_V_DAC.4, PWM_to_V_DAC.6, PWM_to_V_DAC.8, PWM_to_V_DAC.11, PWM_to_V_DAC.12, R2.1, R9.2, RF_IN.2, RF_OUT.2, RF_OUT_LED.1, RF_SWITCH.2, RF_TERM.2, TIMER.1, XOR_GATE.7, XOR_LED.1
unnamed: 5V_LINREG.1, R1.2, R2.2
unnamed: AND_GATE.1, COMPARATOR1.7, R10.1, R15.1, XOR_GATE.1
unnamed: AND_GATE.2, COMPARATOR2.7, R11.1, R16.1, XOR_GATE.2
unnamed: AND_GATE.3, R12.2, R17.1, TIMER.4, TIMER.8
unnamed: AND_LED.2, R17.2
unnamed: C5.1, PWM_to_V_DAC.10
unnamed: C6.1, R14.2, TIMER.2, TIMER.6
unnamed: C7.1, RF_IN.1
unnamed: C7.2, RF_SWITCH.5
unnamed: C8.1, RF_SWITCH.3
unnamed: C8.2, RF_OUT.1
unnamed: C9.1, RF_SWITCH.1
unnamed: C9.2, RF_TERM.1
unnamed: COMP1_LED.2, R15.2
unnamed: COMP2_LED.2, R16.2
unnamed: COMPARATOR1.2, COMPARATOR2.2, PWM_to_V_DAC.2
unnamed: INVERTER.1, R19.2, RF_SWITCH.6, XOR_GATE.8
unnamed: INVERTER.2, RF_SWITCH.4
unnamed: R3.2, R4.1
unnamed: R4.2, R5.1
unnamed: R5.2, R6.1
unnamed: R8.2, R9.1
unnamed: R12.1, R13.2, TIMER.7
unnamed: R13.1, R14.1
unnamed: R18.1, XOR_LED.2
unnamed: R18.2, XOR_GATE.3, XOR_GATE.9
unnamed: R19.1, RF_OUT_LED.2
unnamed: TIMER.3, XOR_GATE.10

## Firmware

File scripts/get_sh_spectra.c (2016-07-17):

/**

Reads from SignalHound, live plotting tool + saves raw data.

Authors:
Hamdi, Jay & Michael 2/13/2015

Compile
g++ get_sh_spectra.c -o get_sh_spectra -lbb_api -lfftw3

**/

#include <cstdio>
#include <iostream>
#include <sys/time.h>
#include <time.h>
#include <unistd.h>
#include <cmath>
#include <vector>
#include <fftw3.h>
#include <signal.h>
#include "bb_api.h"

extern "C"
{
    #include "dislin.h"
};

/////////////////////////////////////////////////////////////////
//			Defined Variables		       //
/////////////////////////////////////////////////////////////////

#define pi 3.141592
#define Fs 80 	  // sampling rate [MSample / second] limited by SH API
#define Ns 299008 // 3.7376 mS of data
#define n_zoom 103

/////////////////////////////////////////////////////////////////
// 		          User Settings                        //
/////////////////////////////////////////////////////////////////


// Integration time in [mS] must be multiple of 3.7376 mS
#define tau 40007.2704 //20003.6352 // 3737.6 //10001.8176 //5000.9088
#define Nfft 1024 //131072 (2^17)
// number of fft points power of 2

float times[Ns]; 		 			// Time Vector
float f [Nfft / 2 ];  //remove DC 		 	// Frequency Vector [MHz]
float f_zoom [n_zoom ];
float fft_output[(Nfft / 2 )]; 	// Frequency Domain Data , remove 0 DC
float avg[(Nfft/2) ]; // average fft_out
float avg_zoom [n_zoom];
float maxmax;
float maxfreq;
//time_t timestamp;
timeval timestamp;

// Sleep time between samples
#define SEC_BETWEEN_SAMPLES 0.2

// Sweep Parameters (in MHz)
#define fcenter 137e6 // Center Frequency in H
#define fspan 5e6

#define y1min 0.600
#define y1max 4.20
#define y1step 0.400

#define y2min 2.800
#define y2max 4.20
#define y2step 0.20

// Detector Mode Settings: "average" or "min-max"
#define detect_mode "BB_AVERAGE"
#define scale "BB_LOG_SCALE"
#define reflvl 0

// Attenuation Mode
#define gain_level 0
#define rbw_val 10e3
#define vbw_val 10e3

/////////////////////////////////////////////////////////////////
//		   Signal Hound Functions		       //
/////////////////////////////////////////////////////////////////

std::vector<double> maxList;
std::vector<double> bufList;
std::vector<double> triggerList;

// Signal Hound parameters
int devID;
unsigned int traceSize;
double binSize, startFreq;
double *min, *max;
//float *buf, *triggers;
//float *samples = new float[Ns]; // 3.7376 mS of Data.

//struct rec ;

//sig_atomic_t volatile run = 'T' ;

// Iterators
int i, j, k;

// Define pointers to (fftw) complex arrays
// which will serve as input and output to the Fourier transforms
//fftw_complex *in, *out ; //, *in_win1 , *in_win2, *out_win1 , *out_win2;
//fftw_plan p; //, p1, p2;



static bool keepRunning = true;

void intHandler(int dummy=0) {
    keepRunning = false;
}
// Initialize, open and configure device.
void sh_calibration()
{

	bbOpenDevice( &devID );
		printf("#Signal Hound Device #: %i\n",devID);

	bbConfigureAcquisition(
		devID,
		BB_AVERAGE,
		BB_LOG_SCALE  // Log scaled results
		);


	bbConfigureCenterSpan(
		devID,
		fcenter,    // 915 MHz center
		fspan // 20 Mhz span is default for raw-pipe mode
		);

	bbConfigureLevel(
		devID,
		0, // not applicable if gain selected
		BB_AUTO_ATTEN   // atten dB, a set attenuation may produce a non-flat noise floor.
		);

	bbConfigureGain(
                devID,
                BB_AUTO_GAIN //BB_AUTO_GAIN //1 // 0// low gain
                );

	bbConfigureSweepCoupling(
		devID,
		rbw_val, // 10 kHz
		vbw_val, // 1 kHz
		0.10,    // 1 second
		BB_NATIVE_RBW, // Use native rbw
		BB_NO_SPUR_REJECT  // No software spur rejection
		);

	bbConfigureWindow(
		devID,
		BB_HAMMING // Hamming windowing functionb
		);

	bbConfigureProcUnits(
		devID,
		BB_POWER  //
		);

}

//I broke up these calls b/c when taking samples it is not necessary to recalibrate, only reinitiate

void sh_init()
{

	bbInitiate(
		devID,
		BB_SWEEPING,
		0
		);

	bbQueryTraceInfo(
		devID,
		&traceSize, // Get trace size, our case power
		&binSize,   // Get freq per returned sample, difference in frequency between values
		&startFreq  // Get accurate start frequency
		);
	min = new double[traceSize];
	max = new double[traceSize];

// To determine the frequency at any point, use the following function
// Frequency of n'th sample point in return sweep=startfreq+n*binsize



	bbFetchTrace(
		devID,
		traceSize,
		min,
		max
		);

}

//compute frequency table
//freq = np.linspace(fcenter-(fspan/2),fcenter+(fspan/2),len(spec['max']))
//peak_power = np.max(spec['max'])
//peak_freq = freq[list(spec['max']).index(float(peak_power))]

/**

void sh_get_samples()
{

	for ( i = 0; i < 10; i++ )
	{
	sh_init();
	bbFetchTrace(
	devID,
	traceSize,
	min,
	max);
		for (j=1; j < 10; j++)
		{
			if(max[i] < max[j])
			{
				max[0]=max[j];
				maxList.push_back(max[i]);
			}
		}20.00
	//Delay(1000);		//time delay of 1000ms, 1 sec. for now takes data for 10 seconds
	for( std::vector<double>::const_iterator i = maxList.begin(); i != maxList.end(); ++i)
    		std::cout << *i << ",  ";
	};


	while( streamingData = TRUE ) {
		bbFetchRaw(
		devID,
		buf,     // spectrum
		triggers // triggers
		);

	// Extract just the trigger positions into a vector
	int i = 0;
	while(buf[i]) {
		bufList.push_back(buf[i]);
		i++;
	}

	//doSomethingWithData( buf, triggerList ); // Save/process/display

}


**/

//the first for loop fetches a trace each second for 10 sec
//the second for loop looks at the max array(peak power) and checks each element to see which is
//larger. It starts with 0,1 and stores the larger value in max[0], then checks the new max[0]
//against max[2] and so forth until the largest element is stored in max[0]


////////////////////////////////////////////////////////////////////////

/**

void s_save()
{
	FILE *fp;

	fp=fopen("/home/SHdata1","w");
	fwrite('%f %f %f \n',traceSize,min,max);
	fclose(fp);
}

**/

void sh_terminate()
{
	printf("#Disconnecting Instrument ...\n");
	bbCloseDevice(devID);
	//printf("Saving remaining data ...\n");

}







/////////////////////////////////////////////////////////////////////////
//	interupt handler
/////////////////////////////////////////////////////////////////////////

/**

class GracefulInterruptHandler(object):

    def __init__(self, sig=signal.SIGINT):
        self.sig = sig

    def __enter__(self):

        self.interrupted = False
        self.released = False

        self.original_handler = signal.getsignal(self.sig)

        def handler(signum, frame):
            self.release()
            self.interrupted = True

        signal.signal(self.sig, handler)

        return self

    def __exit__(self, type, value, tb):
        self.release()

    def release(self):

        if self.released:
            return False

        signal.signal(self.sig, self.original_handler)

        self.released = True


**/

/////////////////////////////////////////////////////////////////
//			Main Method			       //
/////////////////////////////////////////////////////////////////



int main()
{
	min = NULL;
	max = NULL;
	signal(SIGINT, intHandler);
	sh_calibration();
	sh_init();
	//timestamp = time(NULL);
    //timestamp = gmtime(&timestamp);
	//printf("%.2ld",timestamp);
	gettimeofday(&timestamp,NULL);
	printf("%.2f",1.0*(timestamp.tv_sec*1e6+timestamp.tv_usec)/1.0e6);
	// print the frequencies to the top of a text file here
	for (i = 0; i<traceSize; i++)
	{
		printf(",%6.3f ",(i*binSize+startFreq)/1e6);
	}
	printf("\n");
	// start inifinite loop

	while (keepRunning){
		bbQueryTraceInfo(
			devID,
			&traceSize, // Get trace size, our case power
			&binSize,   // Get freq per returned sample, difference in frequency between values
			&startFreq  // Get accurate start frequency
		);

		//min = new double[traceSize];
		//max = new double[traceSize];

		bbFetchTrace(
			devID,
			traceSize,
			min,
			max
			);
		//get the spectrum
		//timestamp = time(NULL); //get the time in secomends since 1970
		//print the time and the spectrum
		//printf("%.2ld",timestamp);
		gettimeofday(&timestamp,NULL);
	    printf("%.2f",1.0*(timestamp.tv_sec*1e6+timestamp.tv_usec)/1.0e6);
		
		for (i = 0; i<traceSize; i++)
		{
			printf(",%6.3f", min[i]);
		}
		printf("\n");
		//printf("#binsize = %6.2f, startFreq = %6.3f  bandwidth=%6.2f\n",binSize/1e3,startFreq/1e6,binSize*traceSize/1e6);
		//printf("%i %f %f \n",traceSize,*min,*max);


		/**
		//Find the max
		maxmax=-1000;
		maxfreq = 0;
		for (i = 0; i<traceSize; i++)
		{
			if (max[i]>maxmax)
			{
				maxmax = max[i];
				maxfreq = i*binSize+startFreq;
			}
		}
		printf("max = %6.3f, freq = %6.3f \n",maxmax,maxfreq);
		**/
		usleep(SEC_BETWEEN_SAMPLES*1e6);
	} //end of the while
	sh_terminate();
	if (min != NULL) delete min;
	if (max != NULL) delete max;

}


//bbFetchRawSweep(devID,*samples); //spectrum is an array with an entry for each channels. 	   This needs to be defined at the top based on your setup. **I believe spectrum will be the 	  samples array

/** Jay/Michael

Don't do the below stuff something in the FFTW usage is messed up. Instead lets use the bbFetchRawSweep function see above.

        in[0][0]=0;//this is causing the program to exit (wihtout any error) Our current compile command is:  g++ SHtest1.c -o SHtest1 -lbbapi -lfftw3 -lm && sudo ./SHtest1
	printf("Running our test_func...\n");
	test_func();
        printf("getting samples...\n");
	sh_get_samples();
	//printf("in[0][0]: %f\n", in[0][0]);
	**/


//Both sweep and raw sweep mode takes a stream of data at 20 Mhz bandwidth
//the difference is that sweep takes continuous data, while raw sweep takes steps with n samples at
//each step of the 20Mhz stream. Raw data mode does the same, only returns 32-bit floats rather
//than the signed shorts of what raw sweep returns




/*

dont need this code




void sig_handler(int signum)
{
  if (signum == SIGINT)
    run = 'F' ;
}

void sh_get_samples()
{
    for ( i = 0; i < Ns; i++ )
    {
          samples[i] = 0 ;
    }
    //printf("fetchingRaw");
    bbFetchRaw(
           devID,
           samples, // spectrum
           NULL // triggers
           );
    for ( i = 0; i < Ns; i++ )
    {
        in[i][0]  =  samples[i];
    }

}
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

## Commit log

2016-05-23 Plot windows for power related plots now autoscale
2016-06-09 Updated post-processing portions of scripts. Tested on ER data for start/stop time and waypoint filtering.
2016-12-16 kill an annoying print statement
2018-07-03 adding a script to calibrate the usrp passband
2018-08-15 Adding x300 calibration notebook
2018-08-15 lengthen DC blocker to 1024 samples
2018-09-20 more calibration analysis
2019-06-14 RFI_Report
    Uploading RFI report for drone switching regulator
    -Mickey
    [X8_reg_rfi_data.csv, X8_reg_rfi_data_adj.csv, pbm_reg_rfi_data.csv, pbm_reg_rfi_data_adj.csv]
2019-10-02 Current position removal
    Removed check that center position was within 100m of hard-coded coordinate
2019-10-03 fixed yaw waypoint
    Added a yaw option to the gen script, and print_MAV_WPT now takes that yaw and prints it before the lat
2019-10-03 1 more undo
    forgot to remove vel from print_MAV_WPT
2020-01-30 Removed report and reduction folders, created temp folder for scripts to keep, updated readme with missing scripts from master script
    [X8_reg_rfi_data.csv, X8_reg_rfi_data_adj.csv, pbm_reg_rfi_data.csv, pbm_reg_rfi_data_adj.csv]
2020-07-28 added mount STLs
    [Chiropter_Adapter_Plate_v1.STL, Chiropter_Adapter_Plate_v2.2.STL, Chiropter_Valon_Mount_v1.STL, Generic_BicoLOG_Mount.STL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]
2020-07-28 added rst summary table
    [ECHO_Summary.csv]
2020-07-28 clean up into 1 rst
    [ECHO_Summary.csv]
2020-08-13 removed references to variables that are no longer used, add HP beam to power variable when created
2020-08-17 rx power dB conversion
2020-10-08 increased test coverate, removed deprecated functions, removed server_utils
    [Shortened_NSTop_ulog_global.csv, Shortened_NSTop_ulog_gps.csv, Shortened_NSTop_ulog_local.csv]
2022-08-29 add chopper
    [ECHO_Chopper_RevF.kicad_pcb, ECHO_Chopper_RevF.sch]
